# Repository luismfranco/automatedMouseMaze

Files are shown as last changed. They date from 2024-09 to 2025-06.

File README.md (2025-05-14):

# Automated Mouse Maze

GUI for behavioral and neurophysiological experiments in an automated maze for mice.  
Currently under development in the [Niell Lab](https://nielllab.uoregon.edu/).

***Disclamimer: the initial designs for this automated maze are based on previous work done at the [Sylwestrak Lab](https://www.sylwestraklab.com/)***

# Installation

## Requirements

1. Operating System: Windows.
2. [Anaconda](https://www.anaconda.com/). Set up its path to [environment variable](https://www.youtube.com/watch?v=Xa6m1hJHba0&ab_channel=DavidRajMicheal).
3. [Git](https://git-scm.com/downloads).
4. [Microsoft Visual C++ 14.0](https://visualstudio.microsoft.com/visual-cpp-build-tools/) or greater.
5. [Arduino IDE](https://www.arduino.cc/en/software/).
6. [StreamCatcherPro](https://www.startech.com/en-us/audio-video-products/usb3hdcap).
7. [Open Ephys GUI](https://open-ephys.org/gui)

## Step by step

In the Command Prompt:
1. Create your environment. Example:  
``conda create -n automatedMouseMaze python=3.10.14 pip``
2. Activate your environment:  
``conda activate automatedMouseMaze``
3. Choose a location where you would like to copy this repo. Example:  
``mkdir Documents\automatedMouseMaze\Application``  
``cd Documents\automatedMouseMaze\Application\``
4. Clone this repository:  
``git clone https://github.com/luismfranco/automatedMouseMaze.git .``
5. Before installing dependencies, you might need to upgrade pip:  
``python -m pip install --upgrade pip``
6. Install dependencies in your environment (this might take a few minutes):  
``pip install .``
7. This code was developed for Python - Teensy 4.0 communication. pyfirmata was developed for Arduino. There is bug in pyfirmata when trying to input the Teensy 4.0 layout. To fix it, run:  
``python src\debugPyFirmata.py``

If everything went well, you should be able to run the GUI:  
``python automatedMouseMaze.py``
<p align="center">
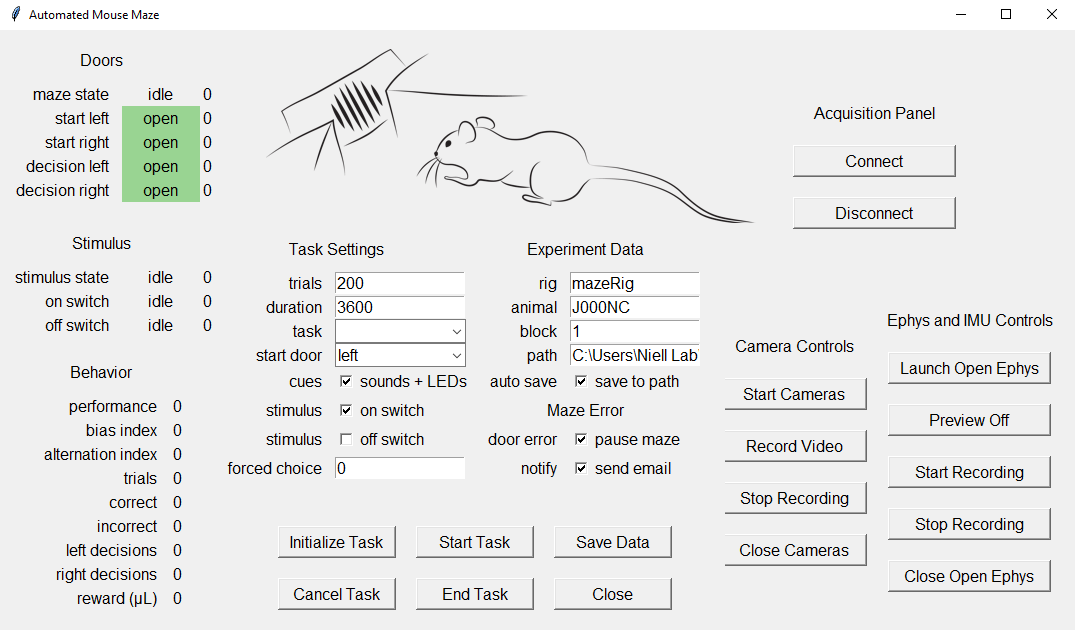
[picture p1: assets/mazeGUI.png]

</p>

However, this app requires a connection with a Teensy board in order to work. Also, the automated maze has several other components, such as IR sensors, solenoid valves, a speaker, and LEDs. To build your own maze, follow this tutorial: 
[maze construction](docs/howToBuildYourOwnMaze.md).

This apps also controls and triggers the recording of video, IMU sensors, and electrophysiology probes. Please refer to [Parker et al., 2022](https://doi.org/10.1016/j.neuron.2022.08.029) for more details on this.

# Configuration Settings

Before running your first experiment, make sure you have uploaded the [Standard Firmata](https://github.com/firmata/arduino/blob/main/examples/StandardFirmata/StandardFirmata.ino) sketch into your Teensy board, which you can find in Arduino IDE at:  
``File --> Examples --> Firmata --> Standard Firmata``

Also, ensure Teensy is properly [configured](config/package.json):
1. Under ``teensyConfiguration``, select the correct serial ``port`` for communication between the computer and Teensy (e.g. ***COM3***).
2. Under ``stimulusScreen``, select the correct ``screenNumber``. In Windows, you can verify the screen number in: ``Display settings > Display > Identify``.
3. There are also a number of input and output digintal pins under ``teensyConfiguration``. Make sure they are properly assigned according to your electronic circuit (see example below).

## Example board with connections for Teensy pins

1. Solenoid valves, including transistors and diodes. The solenoids for the maze doors (green wires) require a 24 V power supply. The solenoids for the water rewards (blue wires) require a 12 V power supply. **Important: use diodes to make sure current doesn't flow back from solenoids to Teensy**. In this example, the configuration is:  
   ``"leftStartDoor": "5"``  
   ``"rightStartDoor": "7"``  
   ``"leftDecisionDoor": "9"``  
   ``"rightDecisionDoor": "11"``  
   ``"leftWaterPort": "1"``  
   ``"rightWaterPort": "3"``  
2. IR sensors, including a connection between their white signal wire and the 5V power supply (see the bottom view of the circuit below). In this example, the configuration is:  
   ``"leftStartIRsensor": "22"``  
   ``"rightStartIRsensor": "20"``  
   ``"leftDecisionIRsensor": "18"``  
   ``"rightDecisionIRsensor": "16"``  
   ``"startStimulusIRsensor": "15"``  
   ``"stopStimulusIRsensor": "14"``  
3. LEDs, including transitors diodes and resistors. LEDs require a 5 V power supply. In this example, the configuration is:  
   ``"leftLED": "0"``  
   ``"rightLED": "2"``  

<p align="center">
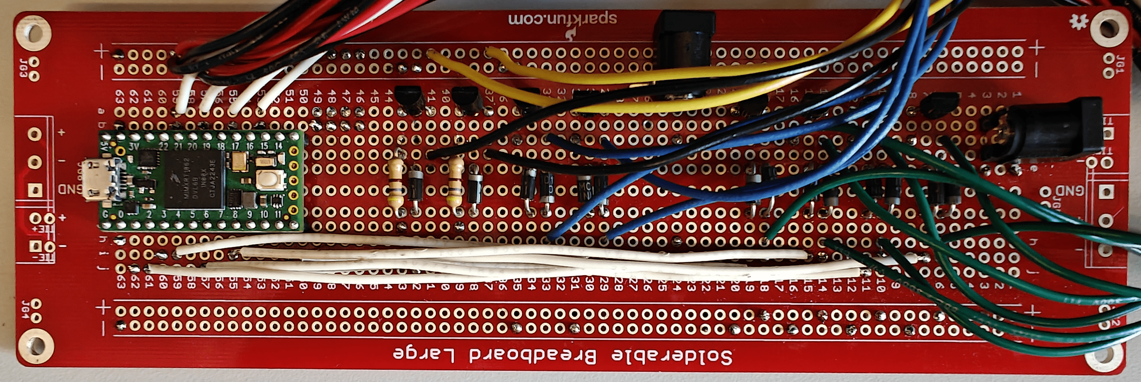
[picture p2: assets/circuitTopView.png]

</p>
<p align="center">
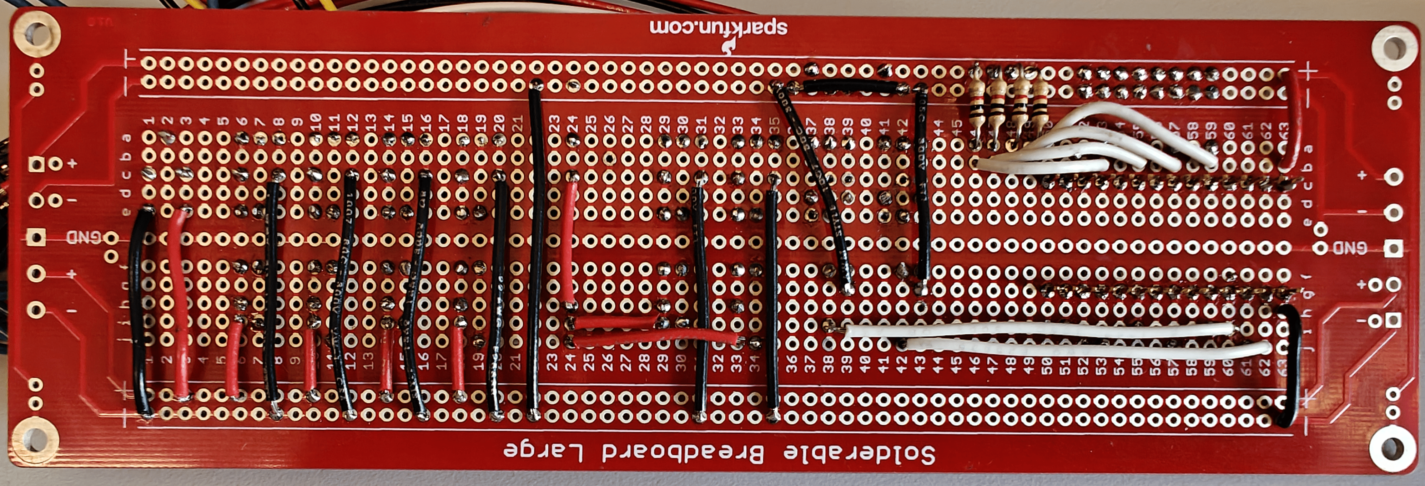
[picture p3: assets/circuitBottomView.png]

</p>

# How to Run this App

In the Command Prompt, activate your environment. Example:  
``conda activate automatedMouseMaze``  
Then, cd to the location where this app was installed, and then type:  
``python automatedMouseMaze.py``

You could also create a batch file. Example:  
``call activate automatedMouseMaze``  
``cd C:\Users\Niell Lab\Documents\automatedMouseMaze\Application\``  
``python automatedMouseMaze.py``  

# Before Running an Experiment

Under ``task``, please select ``valveCalibration`` and click on ``Initialize Task``. This will open a small window with three parameters:

<p align="center">
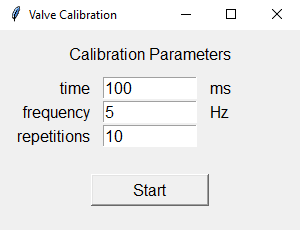
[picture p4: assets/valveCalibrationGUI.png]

</p>

1. ``time`` for the opening water valves (in ms).
2. ``frequency`` for valve openning repetitions (in Hz). Make sure ``frequency`` is slow enough to allow the full openning ``time`` in each repetition.
3. Number of ``repetitions``. The shorter the ``time`` the more ``repetitions`` are needed to minimize measurement errors.

Example parameters for a calibration curve are displayed in the terminal every time ``valveCalibration`` is initialized:  
``Time:           5,  10,  15,  20,  25,  30,  40,  50,  60,  80, 100``  
``Frequency:     25,  25,  20,  15,  15,  15,  10,  10,   5,   5,   5``  
``Repetitions: 1500, 750, 500, 400, 300, 250, 200, 150, 125, 100,  50``  

Once you have calculated the correct valve opening time for 5, 6, 7, 8, 9 and 10 μL, you can update the ``src/mazeGUI.py`` script in the "Reward" subsection of the ``__init__`` method in the  ``class mazeGUI``:  
``self.estimatedReward = 0``  
``self.leftRewardStreak = [32, 36, 41, 45, 49, 54] # in ms``  
``self.rightRewardStreak = [32, 37, 41, 46, 50, 55] # in ms``  
``self.rewardAmounts = [ 5,  6,  7,  8,  9, 10] # in μL``  

# How to Run an Experiment

There are a few options you can select before running an experiment.

## Task Settings

1. Maximum number of ``trials``.
2. Maximum ``duration`` of the experiment (in seconds).
3. The particular visual stimulus, under ``task`` (more details below).
4. The location of the animal at the start of the session, under ``start door``. This is the door that will open for the first trial.
5. Sounds and light ``cues`` for helping during learning of the task.
6. Triggering the display of the visual ``stimulus`` on the screen.
7. Turning off the display of the visual ``stimulus``.
8. Fraction of trials with ``forced choice``, where only the door for the correct decision is opened. Helpful during early stages of training.

## Experiment Data

1. Name of your ``rig``.
2. Name of your ``animal``.
3. ``block`` number.
4. ``path`` for saving the experiment data.
5. ``autoSave`` option.

Once your have selected your desired options, you can click on ``Initialize Task``. This will establish a connection between the computer and Teensy. It will also initialize the visual stimulus in the background, but it will not show it yet. Clicking on ``Initialize Task`` disables all fields in the "Task Settings" and "Experiment Data" boxes. If you would like to change something, click on ``Cancel Task``. This will allow you to access all fields again, but you will need to ``Initialize Task`` again afterwards.

Next, clikc on ``Start Task`` to start running your experiment. If you would like to record video and do electrophysiology as well (see below), make sure you have initialized those options before clickin on ``Start Task``. After a task has started, only the door selected in ``start door`` (see above) will open, and the visual stimulus will be displayed on the screen throughout the trial, unless the on and/or off switchs are enabled (see above).

If you would like to stop the task prematurely (i.e., before reaching the maximum trial number or the maximum duration), click on ``End Task``.

At the end of each experiment, if ``auto save`` is enabled, data are automatically saved. Also, if ``auto save`` is not enabled, or in case of an unexepcted crash (and if the GUI is still available), you can click on ``Save Data`` to manually save your experiment data.

To close the app GUI, click on ``Close`` or on the upper right "X".

# Camera Controls

Before using the cameras for the first time, make sure you have set their IDs properly under ``crownCameras`` in the [configuration](config/package.json) file. You can find their IDs by running this script in the Command Prompt:  
``python src\findCameras.py``  

1. ``Start Cameras`` opens a preview window for the eye and the world cameras, which record the movement of one eye of the mouse and the world in front of its head, respectively. This preview also creates temporary files in the ``path`` for saving data. Data will only be permanently saved if the ``Record Video`` button is pressed.
2. ``Record Video`` starts the recording of video from both the eye and the world cameras.
3. ``Stop recording`` stops the recording of video in both cameras.
4. ``Close Cameras`` closes the preview window.

***Important: make sure you start your video recordings before starting your task to avoid losing data***

# Ephys and IMU Controls

Before you can use these controls, make sure you have installed the [Open Ephys GUI](https://open-ephys.org/gui). Please refer to the Open Ephys [documentation](https://open-ephys.github.io/gui-docs/) to learn more about this GUI. For instance, you can begin by dragging and adding: 1) an acquisition board, 2) a record node, and 3) an LFP viewer to the signal chain at the bottom of the GUI from the list of processors on the left pannel.

<p align="center">
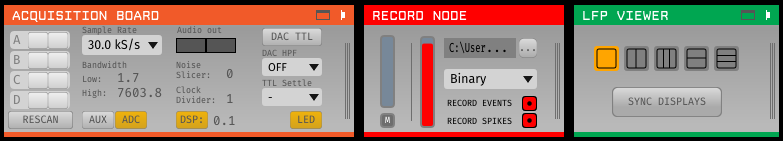
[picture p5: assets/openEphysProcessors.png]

</p>

Once you have done that, you can control the Open Ephys GUI with the buttons in the Automated Mouse Maze GUI. 

1. ``Launch Open Ephys`` launches the GUI. The GUI automatically detects the inputs to the Open Ephys acquisition board. For instance, it will automatically detect the HDMI input from the I/O board (carrying data from the IMU), and the Intan cable (carrying data from the neural probe).
2. ``Preview Off`` switches to ``Preview On`` upon clicking on it. This function allows you to see ongoing neural activity and IMU signals without the need to record them.
3. ``Start Recording`` starts a new recording.
4. ``Stop Recording`` stops recording in progress. Data are automatically saved once the recording is stopped.
5. ``Close Open Ephys`` closes the Open Ephys GUI.

***Important: make sure you start your ephys recordings before starting your task to avoid losing data***

# Task

As mentioned above, the option ``task`` allows you to select between 4 different built-in tasks:

1. Drifting gratings (based on Psychopy [https://github.com/psychopy/psychopy]).
2. Motion selectivity (based on Psychopy [https://github.com/psychopy/psychopy]).
3. White noise (based on OpenCV https://github.com/opencv/opencv).
4. Object discrimination (based on Pygame [https://github.com/pygame/pygame], and on ModernGL [https://github.com/moderngl/moderngl]).
5. There is also another option for calibrating your solenoid valves (see section above).

It is easy to change the settings for the [drifting gratings](src/driftingGratings.py), [motion selectivity](src/motionSelectivity.py) and [white noise](src/whiteNoise.py) tasks under their respective ``initializeStimulus`` and ``startStimulus`` methods. Please refer to Psychopy documentation to learn more about the available options for [GratingStim](https://www.psychopy.org/api/visual/gratingstim.html) and [DotStim](https://www.psychopy.org/api/visual/dotstim.html).

# While Task is Running

The app GUI displays general maze information and behavior stats on the left-hand side that continuously update through the experiemntal session.

## Doors

1. ``maze state``. (0) *ready*, before session starts running, (1) *start*, once a trial has started, (2) *end*, once the mouse has made a decision, (3) *ITI-left*, mouse is on the left side of the maze, waiting for the *left start door* to open, (4) *ITI-right*, mouse is on the right side of the maze, waiting for the *right start door* to open.
2. ``start left``. displays *open* or *closed* for the *left start door*. It also displays the state of its corresponding beam break, a (0) indicates the mouse is passing through its beam break, otherwise it shows (1).
3. ``start right``. same, but for the *right start door*.
4. ``decision left``. same, but for the *left decision door*.
5. ``decision right``. same, but for the *right decision door*.

## Stimulus

1. ``stimulus states``. (0) *ready*, before session starts running, (1) a trial has started, it can display *on* or *off* depending on the configuration for the stimulus *on switch*, (2) *on*, either the stimulus has been on since trial start, or the stimulus just turned on when the mouse passed the *on switch* beam break, (3) the mouse just passed the *off switch* beam break, it can display *on* or *off* depending on the configuration for the stimulus *off switch*, (4) waiting for a decision to be made, (5) "ready", ITI, waiting for a new trial to begin.
2. ``on switch``. if its box is checked, it will display when the stimulus is turned "on" and "off" by the corresponding beam breaks.
3. ``off switch``. if its box is checked, it will display "on" when the stimulus is intentionally turned off by the second beam break in the central corridor of the maze. It will display "off" once a decision has been made by the mouse.

**Note: positioning the beam breaks for the *on* and *off* switches along the central corridor of the maze allows for different experimental configurations, where attention to the visual stimuli can be triggered at different locations, or, to test working memory, the visual stimulus can also be removed at different locations.**

## Behavior

1. ``performance``. Mouse performance, calculated as *P = C / (C + I)*, where *C* and *I* are the total number of correct and incorrect decisions, respectively.
2.  ``bias index``. Decision bias, calculated as *BI = (L - R) / (L + R)*, where *L* and *R* are the total number of left and right decisions, respectively.
3.  ``alternation index``. Rate of switching between decisions (e.g. L, R, L, R, L, R, ...), calculated as *AI = sum(abs(diff(D)))/length(D)*, where *D* is a sequence of zeros and ones corresponding to L and R decisions.
4.  ``trials``. Trial number.
5.  ``correct``. Number of correct decisions.
6.  ``incorrect``. Number of incorrect decisions.
7.  ``left decisions``. Number of decisions to the left.
8.  ``right decisions``. Number of decisions to the right. 
9.  ``reward (μL)``. Estimated reward, based on the parameters obtained by the calibration curve.

# Behavior Data File

Data are automatically saved at the end of a session in the desired path as a pickle file. This file contains a Pandas DataFrame with the following fields:

1. ``trial`` number.
2. ``startDoor`` for each trial. (0) for left, (1) for right.
3. ``leftTargetProbability`` for each trial. Probability for displaying the target object associated with the left decision.
4. ``target`` object for each trial. (0) for left, (1) for right.
5. animal's ``decision`` for each trial. (0) for left, (1) for right.
6. ``forcedChoice`` for each trial. (0) for no forced choice, (1) for forced correct choice.
7. ``correct`` trial identifier. (0) for incorrect trial, (1) for correct trial.
8. ``trial type``: identifier for correct left (1), incorrect right (2), incorrect left (3), or correct right trials (4).
9. ``startTime``. Time stamp for the start of each trial: opening of start door.
10. ``endTime``. Time stamp for the end of each trial: closing of decision door.
11. ``stimulusStartTime``. Time stamp for the display of the visual stimulus on the screen (if option is enabled).
12. ``stimulusEndTIme``. Time stamp for turning off the display of the visual stimulus (if option is enabled).
13. ``taskRawStartTime``. Time stamp for the start of the task. Important for synchronization with video and electrophysiology recordings.

In addition, **task settings** and **visual stimulus parameters** are saved in the same DataFrame. These include the input values for the fields in ``task settings`` and ``experiment data``, the values for water rewards obtained from the ``calibration curves``, as well as specific parameters for the **visual stimulus** defined by the corresponding ``task``.

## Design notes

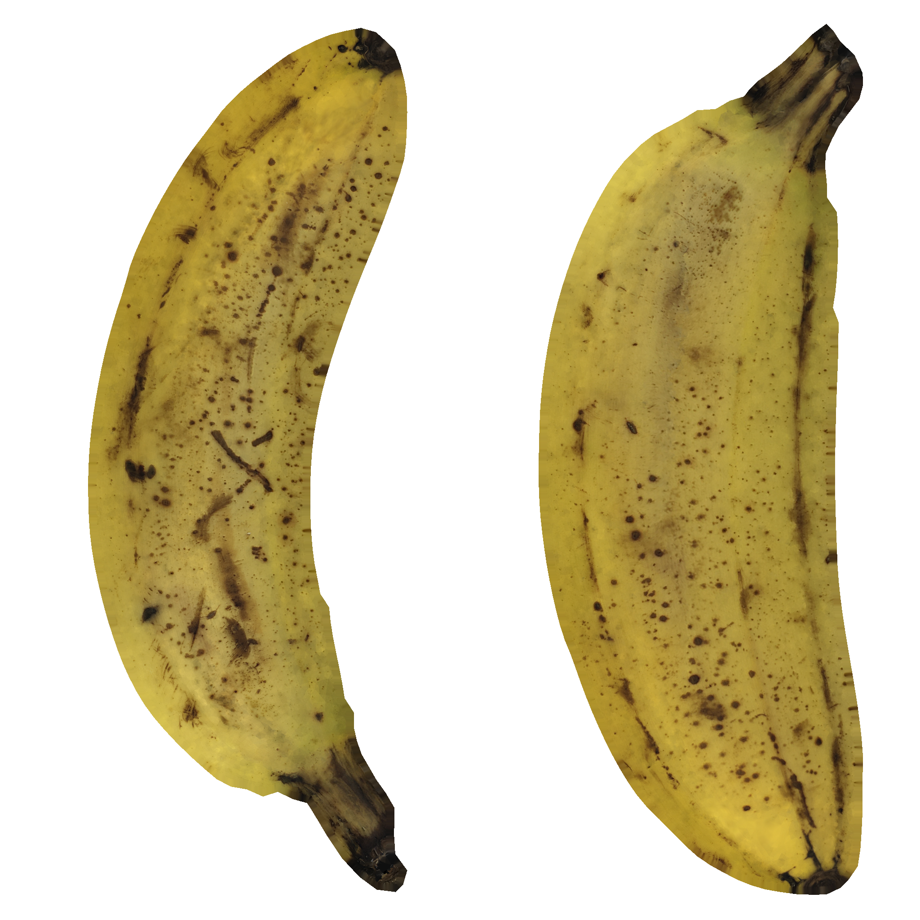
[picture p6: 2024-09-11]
assets/banana/banana.png

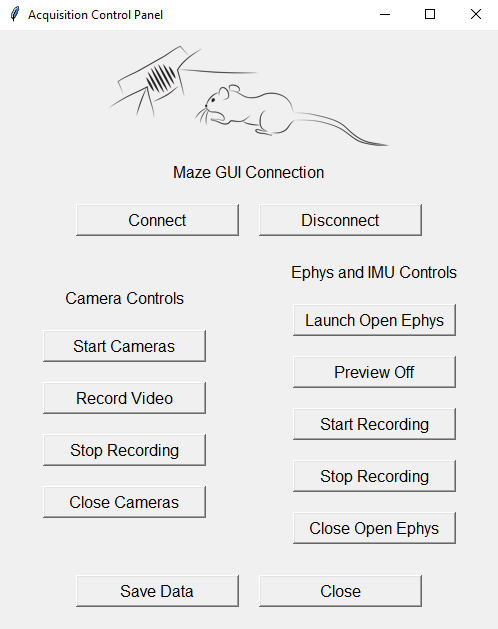
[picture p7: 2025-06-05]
assets/acquisitionControlPanelGUI.png

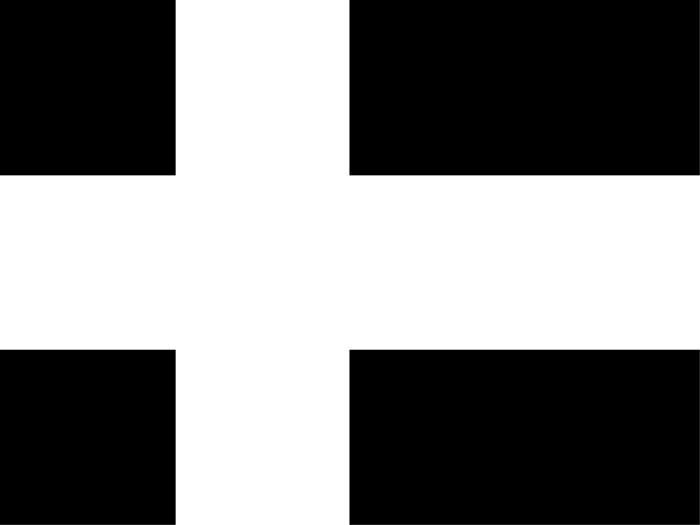
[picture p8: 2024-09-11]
assets/whitebox/whiteBox.png

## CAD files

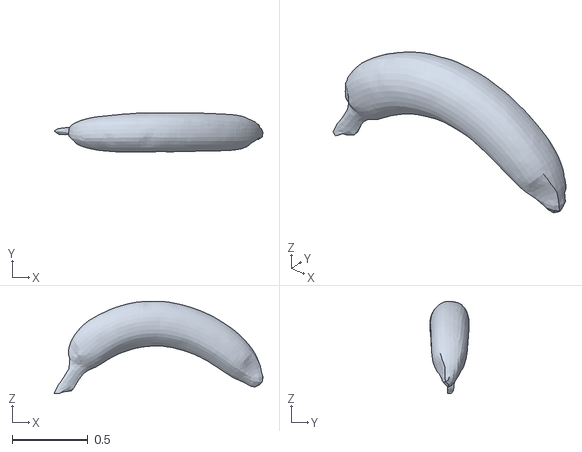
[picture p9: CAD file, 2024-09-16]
assets/banana/banana.obj
1.38 x 0.26 x 0.61

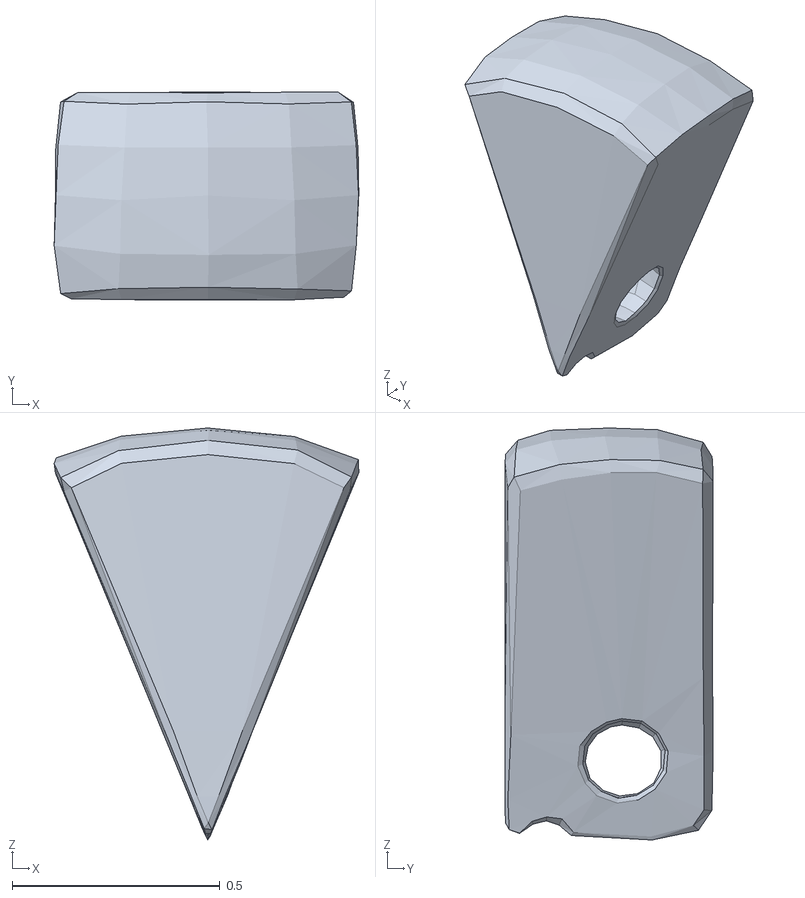
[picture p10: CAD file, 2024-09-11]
assets/cheese/cheese.obj
0.733 x 0.502 x 0.991

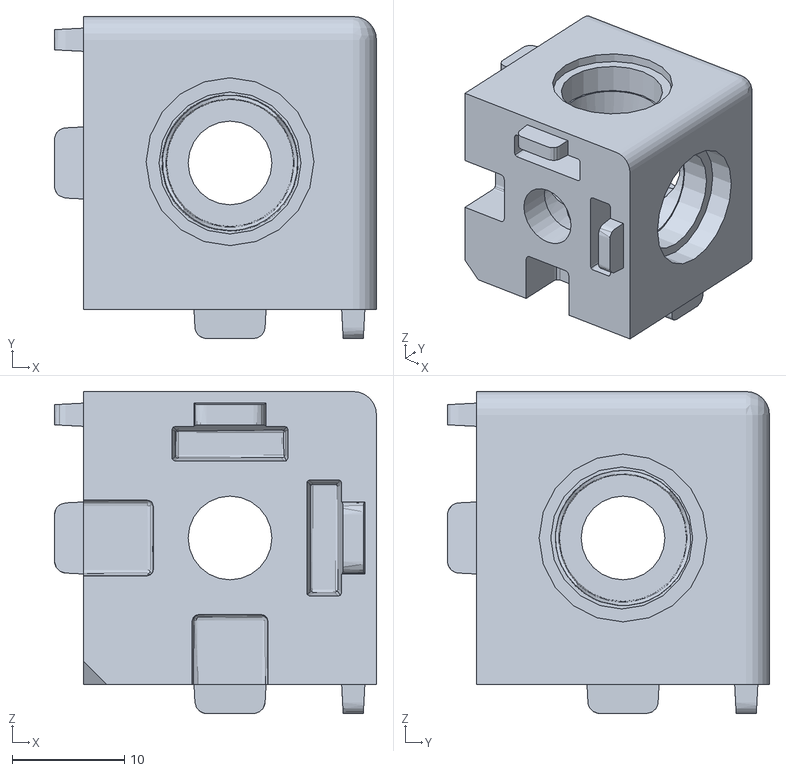
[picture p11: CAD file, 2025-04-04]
assets/hardware/cornerEndBraket.stl
28.8 x 28.8 x 28.8

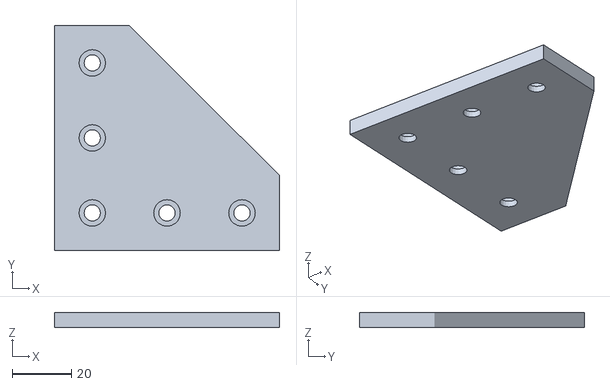
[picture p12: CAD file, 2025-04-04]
assets/hardware/cornerSurfaceBracket.stl
76.2 x 76.2 x 5.00

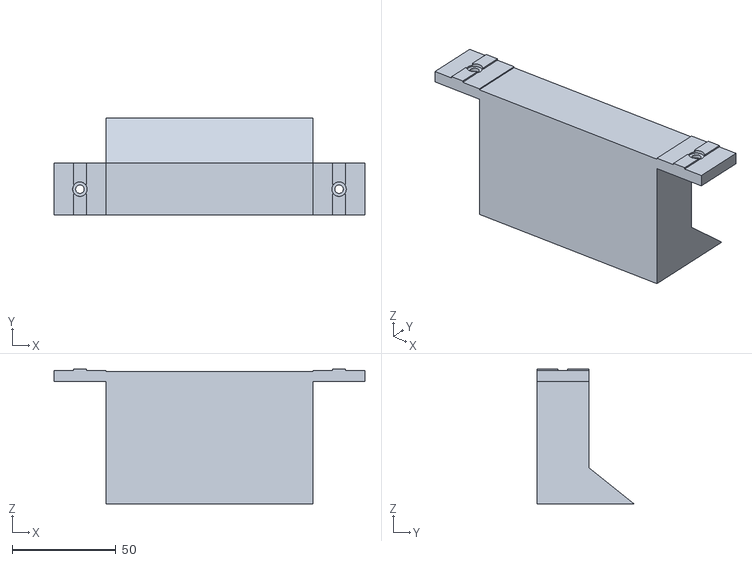
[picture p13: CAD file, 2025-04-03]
assets/hardware/doorFloorStop R.stl
150.0 x 46.8 x 65.0

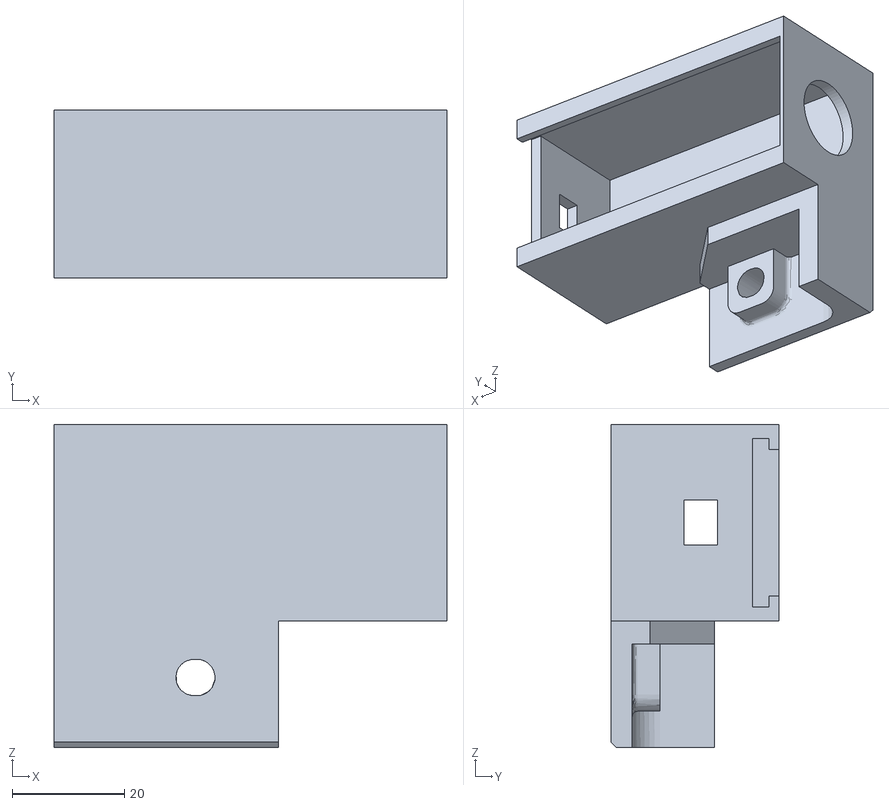
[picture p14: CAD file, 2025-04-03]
assets/hardware/waterButtonBox L.stl
70.0 x 30.0 x 57.6

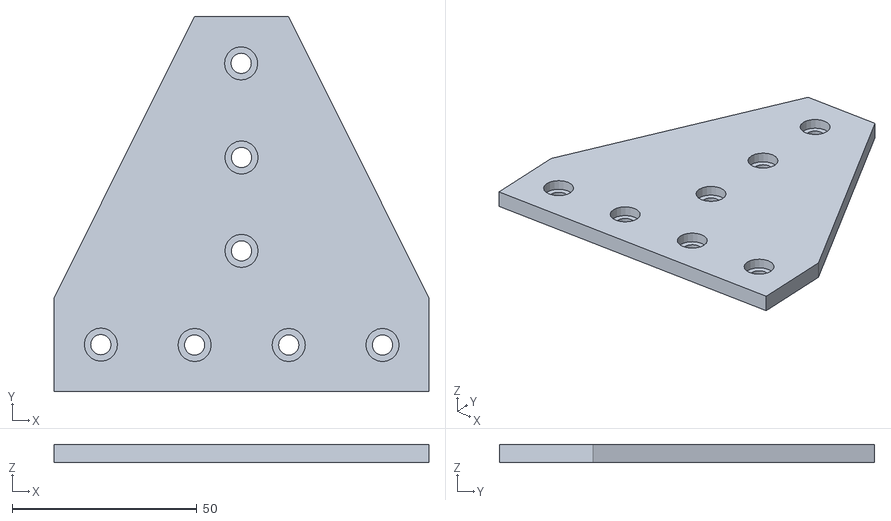
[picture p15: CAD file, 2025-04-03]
assets/hardware/surfaceBracket.stl
101.6 x 101.7 x 5.00

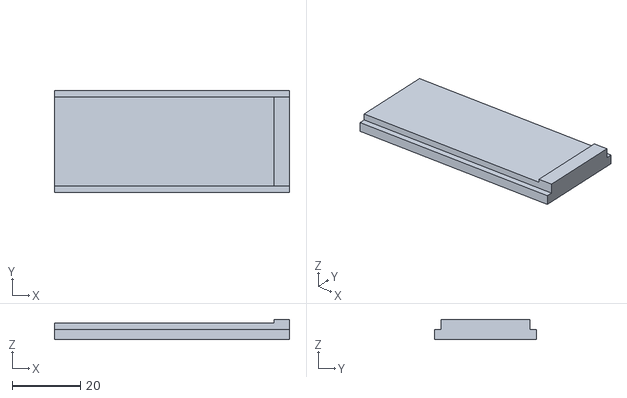
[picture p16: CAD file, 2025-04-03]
assets/hardware/waterButtonBoxLid.stl
69.0 x 30.0 x 5.90

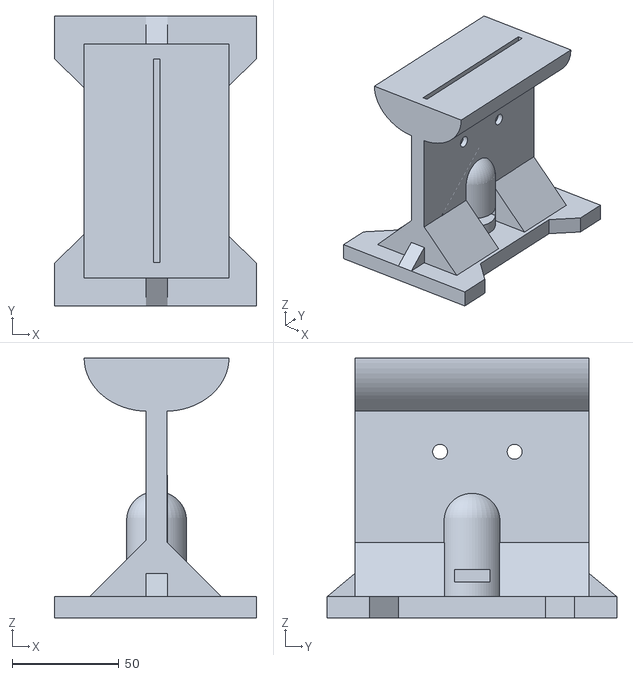
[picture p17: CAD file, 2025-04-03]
assets/hardware/doorHolder.stl
95.0 x 136.0 x 122.0

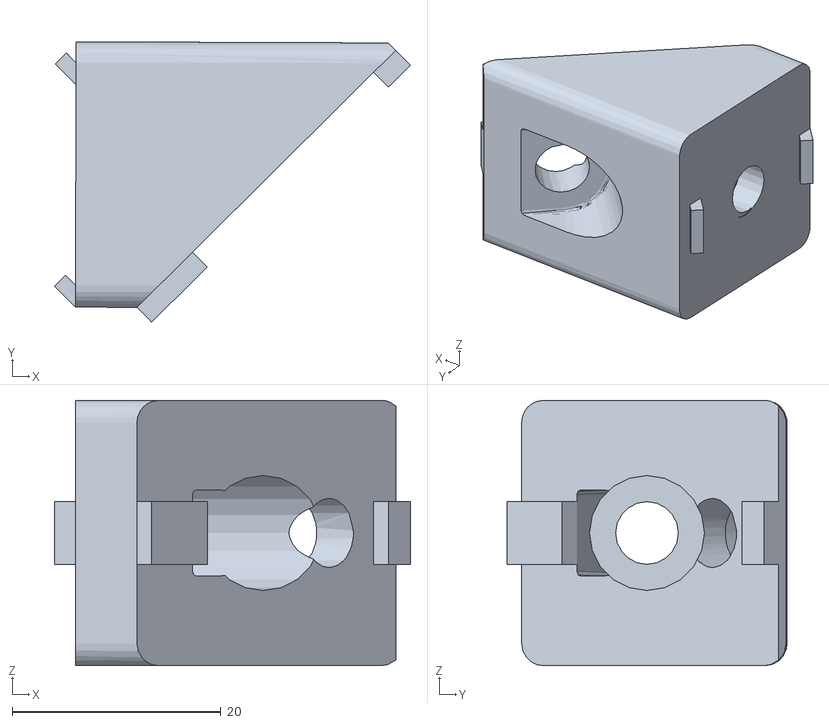
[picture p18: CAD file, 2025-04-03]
assets/hardware/45degreeBracket.stl
34.1 x 26.8 x 25.4

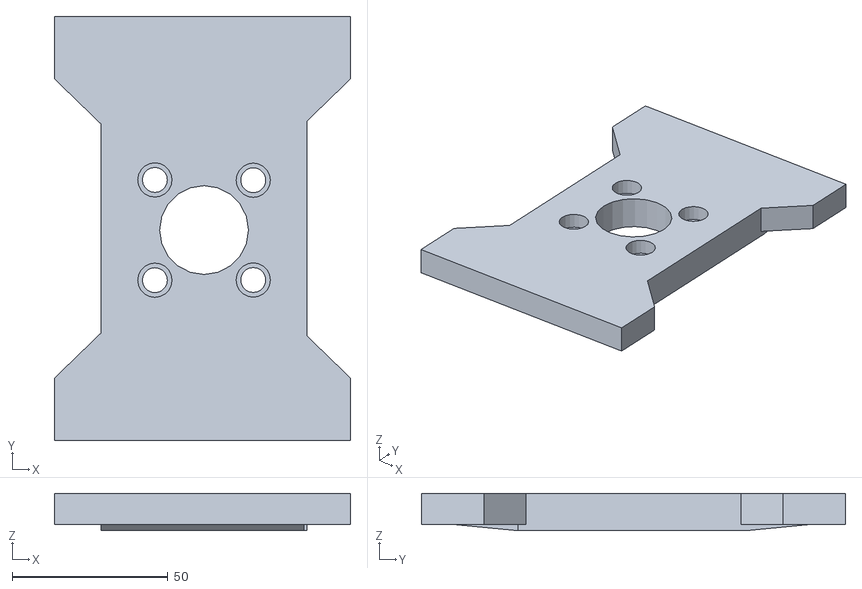
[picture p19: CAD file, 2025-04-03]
assets/hardware/doorCylinderStop.stl
95.0 x 136.0 x 12.0

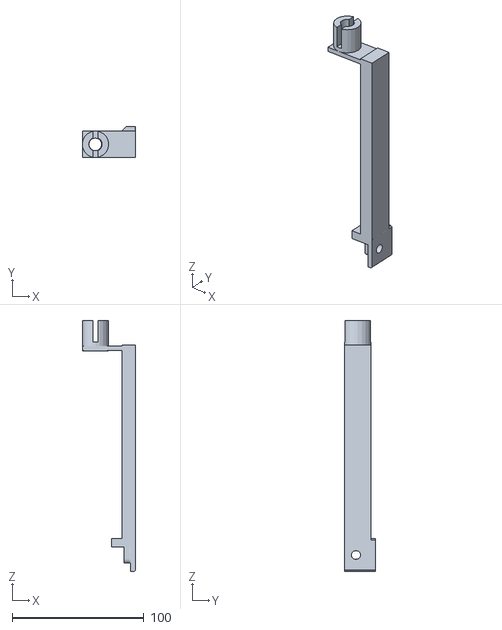
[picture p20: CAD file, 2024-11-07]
assets/hardware/syringeHolder.stl
40.5 x 23.5 x 190.2

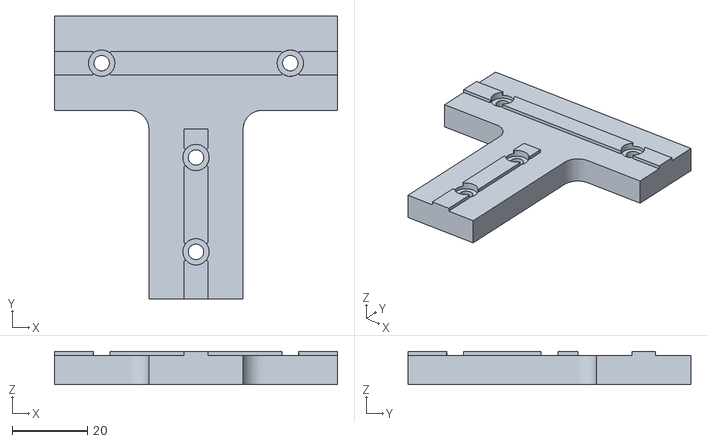
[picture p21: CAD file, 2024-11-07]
assets/hardware/Tbracket.stl
75.0 x 75.0 x 8.75

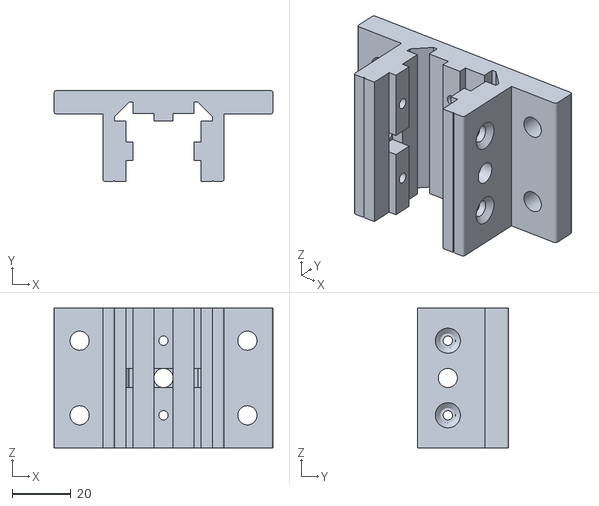
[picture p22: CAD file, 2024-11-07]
assets/hardware/TslottedSleeve.stl
74.6 x 30.9 x 47.6

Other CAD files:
assets/hardware/doorFloorStop L.stl
assets/hardware/waterButtonBox R.stl
assets/hardware/cylinderMountingBase.stl
assets/hardware/waterPort.stl
assets/hardware/IRsensorHolder L.stl
assets/hardware/IRsensorHolder R.stl
assets/hardware/circuitBox.stl
assets/hardware/circuitBoxLid.stl
assets/hardware/screenHolders.stl
assets/hardware/valveHolder.stl

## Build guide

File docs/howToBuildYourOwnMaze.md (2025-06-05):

# Maze Construction

This tutorial describes how we built our autoamted maze in the [Niell Lab](https://nielllab.uoregon.edu/).

***Important: this tutorial is currently under development***

<p align="center">


</p>

# Components

## Maze

1. 1" T-slotted [squared](https://www.mcmaster.com/47065T101/) and [rounded](https://www.mcmaster.com/3136N27/) framing rails, cut to a custom size with 1/4"-20 threads on both ends.
2. Sign white 9 % light transmission [acrylic](https://www.tapplastics.com/product/plastics/cut_to_size_plastic/acrylic_sheets_color/341) for the floor, walls and doors of the maze.
3. 1" [brakets](https://www.mcmaster.com/47065T236/) and [cubes](https://www.mcmaster.com/47065T244/) to assemble the structural frame of the maze.
4. A white melamine [wood shelf](https://www.homedepot.com/p/White-Melamine-Wood-Shelf-23-75-in-D-x-48-in-L-252297/202089063) with 2" [caster wheels](https://www.amazon.com/Casters-Locking-Castors-Furniture-Kitchen/dp/B09QZMTSCQ/ref=pd_bxgy_img_d_sccl_2/142-9516444-0421340?pd_rd_w=h5m3x&content-id=amzn1.sym.839d7715-b862-4989-8f65-c6f9502d15f9&pf_rd_p=839d7715-b862-4989-8f65-c6f9502d15f9&pf_rd_r=FRMHFY3ZBWA5QW7X6ASM&pd_rd_wg=8v5Oh&pd_rd_r=5618abc9-7d00-4d7a-a696-668fa49b88b9&pd_rd_i=B0BFXLTQNH&th=1) for the base of the maze.
5. A 10" [screen](https://www.amazon.com/dp/B0987468N2/ref=sspa_dk_detail_4?pd_rd_i=B0987468N2&pd_rd_w=QqC5K&content-id=amzn1.sym.386c274b-4bfe-4421-9052-a1a56db557ab&pf_rd_p=386c274b-4bfe-4421-9052-a1a56db557ab&pf_rd_r=1QH3Q0EH5X5P3PGTJ3EK&pd_rd_wg=wrki0&pd_rd_r=280cd8b9-b4b4-4a81-84ca-9a71bb273634&s=pc&sp_csd=d2lkZ2V0TmFtZT1zcF9kZXRhaWxfdGhlbWF0aWM&th=1) for displaying visual stimuli.
6. Mini USB [speaker](https://www.adafruit.com/product/3369?gclid=Cj0KCQjw9fqnBhDSARIsAHlcQYQN7-PUcKRt7g5K4LZLOxeUrOmGBO-mkdPEippvQnJ8RdAV6c8ZS8oaAvPWEALw_wcB) for signaling correct and incorrect trials.
7. Diffused 5 mm [LEDs](https://www.adafruit.com/product/4203?gclid=Cj0KCQjw9fqnBhDSARIsAHlcQYQOVymyhPb8JML-s9yA5havhJG0yBzvc3udh55acPwMJ-_8xEU4wKcaAnpeEALw_wcB) for signaling correct trials.
8. [Solenoid valves](https://www.theleeco.com/industries/scientific-instruments/products/solenoid-valves/browse/?filters[subtype][]=Control+Solenoid+Valves) for control of water delivery.
9. 1/16" ID x 1/8" OD Tygon [tubing](https://www.usplastic.com/catalog/item.aspx?itemid=91104&catid=864) for the water delivery system.
10. 14 gauge luer-lock blunt tip [needles](https://www.amazon.com/Syringe-Dispensing-Needles-Length-Interface/dp/B07DZC225B/ref=pd_ci_mcx_di_int_sccai_cn_d_sccl_2_1/133-0408013-9182656?pd_rd_w=JuARf&content-id=amzn1.sym.751acc83-5c05-42d0-a15e-303622651e1e&pf_rd_p=751acc83-5c05-42d0-a15e-303622651e1e&pf_rd_r=SDJGVFYGQZ0KS2EZG109&pd_rd_wg=XP1nb&pd_rd_r=9ea53b80-e963-4a30-bfc5-857ae6b058f9&pd_rd_i=B07DZC225B&psc=1) as spouts for water delivery.
11. Custom [3D-printed objects](https://github.com/luismfranco/automatedMouseMaze/tree/99c225861e82ac3776c7e1dc496d73c4fc0f3bcc/assets/hardware) as rail brakets, sections of walls (i.e., water ports, stimulus screen holders), and to mount other components (i.e., IR sensors, speaker, cables, water system).
12. A blackout [curtain](https://evertrack.co/blackout-room-divider-curtain-eclipse-satin/?utm_term=&utm_campaign=PMAX+-+Room+Divider+Curtains&utm_source=adwords&utm_medium=ppc&hsa_acc=5806130293&hsa_cam=22123857351&hsa_grp=&hsa_ad=&hsa_src=x&hsa_tgt=&hsa_kw=&hsa_mt=&hsa_net=adwords&hsa_ver=3&gad_source=1&gclid=Cj0KCQjw4v6-BhDuARIsALprm32yAWsM92bhXs5Hm0Y3QMyoQlhOliOSD0VcVHp_9gU-yHXiStgtKXEaAvcoEALw_wcB) and [rail](https://www.amazon.com/dp/B0C69LGQW1/ref=sspa_dk_detail_2?pd_rd_i=B0C69LGQW1&pd_rd_w=YEFyC&content-id=amzn1.sym.386c274b-4bfe-4421-9052-a1a56db557ab&pf_rd_p=386c274b-4bfe-4421-9052-a1a56db557ab&pf_rd_r=B9N6694BX21GFFRSVHP6&pd_rd_wg=QsIWq&pd_rd_r=c0aed70f-5ff7-4f5d-a2dd-321a2899c61f&s=kitchen&sp_csd=d2lkZ2V0TmFtZT1zcF9kZXRhaWxfdGhlbWF0aWM&th=1) to isolate the maze and mice from external distractions.

## Automated Doors

1. [Pneumatic actuators](https://www.amazon.com/Baomain-Pneumatic-Cylinder-SC-Screwed/dp/B01F9XZQ1K/ref=pd_ci_mcx_di_int_sccai_cn_d_sccl_2_2/136-8001444-7379768?pd_rd_w=CoJWI&content-id=amzn1.sym.751acc83-5c05-42d0-a15e-303622651e1e&pf_rd_p=751acc83-5c05-42d0-a15e-303622651e1e&pf_rd_r=AXNT0SNVR13YJT89ZTJJ&pd_rd_wg=F8NEU&pd_rd_r=9dcf470c-de43-4689-a980-ca5e8e994869&pd_rd_i=B01F9XZQ1K&th=1) for movement of the automated doors.
2. A [solenoid manifold](https://www.amazon.com/Baomain-4V210-08-Position-Pneumatic-Solenoid/dp/B01D9IGCTC/ref=sims_dp_d_dex_ai_speed_loc_mtl_v4_d_sccl_4_1/136-8001444-7379768?pd_rd_w=QAJm3&content-id=amzn1.sym.af515e1d-64ab-47a5-8a2e-6be4d0f4cdc5&pf_rd_p=af515e1d-64ab-47a5-8a2e-6be4d0f4cdc5&pf_rd_r=QQ6ZJF00XSNFZP6H8B3Z&pd_rd_wg=ip6Yj&pd_rd_r=6282a60c-3df6-4d58-8258-af29a286d7ae&pd_rd_i=B01D9IGCTC&psc=1) for controlling the automated doors.
3. [6 mm](https://www.amazon.com/Tailonz-Pneumatic-Black-Polyurethane-32-8ft/dp/B08GC6TR2S/ref=sr_1_6?crid=B4SJCL6S8C9C&dib=eyJ2IjoiMSJ9.DejGkL7N9ogqAzdCGOySW8Ul4oFXYI6uTvpMsLFLQavsPcgyc9dCZSS0RZEDuOVTGBNc74dp5AgyndprPP87Hf5uJyTtiH9rcP7fQU8OTkzCA8K8Lv6_3velU18rnE5GaAfLZ6q1gyariRIkULl7URyfKc2KDw0pVo_LMPqGbvt8MmwsfXPHnCfzkYaMb4eLXCrkmvK0VoPedBBdU368PWvUj1i6hELtX5D_il5MeDzO23k3WryqV_aB2wbEvVOaP6Nks4V_xsxegeLF3uYnt_uTJ9Vwoqsxe3ukTBuhLVI.ajZ5AaE_mu1l8TI9caTWLeYIIOOZVvQAvAvGWvogzXg&dib_tag=se&keywords=Air%2BLine%2BTubing%2BKit%2B6mm%2Bblack&qid=1714772204&s=industrial&sprefix=air%2Bline%2Btubing%2Bkit%2B6mm%2Bblac%2Cindustrial%2C121&sr=1-6&th=1) and [8 mm](https://www.amazon.com/CGELE-Pneumatic-Transfer-OD-39-4Ft-12Meter/dp/B09LS1S7MK/ref=sr_1_3?crid=1UCLWG8RC00F5&dib=eyJ2IjoiMSJ9.9IT0mdNrbcPPwFnwS3lttd1-X4Lt2TRh2Ekuy9jjREetTrO9R6abyOPbWKJOIBw0.COukHekBEaDTeMd4yj45MHDLXDYYBJPRxJqthZbJgoc&dib_tag=se&keywords=TAILONZ%2BPNEUMATIC%2BBlack%2B5%2F16&qid=1724450805&s=hi&sprefix=tailonz%2Bpneumatic%2Bblack%2B5%2F1%2Ctools%2C144&sr=1-3&th=1) tubing for air connections, as well as [adapters](https://www.amazon.com/Metalwork-Straight-Reducing-Pneumatic-Connector/dp/B07C7BGQ9S/ref=sr_1_5?crid=2EOM3OXEO5504&dib=eyJ2IjoiMSJ9.sZVireplGplt2H6sWKEogbyxddOqDaPAou-Hecj9GtV1WioAia-WJQIGtxOWdVFVTQup_Kqhm3tuUmI4i797ggSqxKtK6BQcITqGEm_J8Jd80-lc9OO1TKfBGQq-wL9LLAby1xOZYYVYpjkhlgDVuNfve2of7sbq0TFmEraXme2kNnz8YlwITV7zWLn_CfpviRaNwQc0ZqtmgVXMZVcHYADlHSF5U06SYpBPrxmvLaM.iJ10JiNAwGi4COcf2CwCBSLYdg1aO_1qU6pIi8fo8Nk&dib_tag=se&keywords=10%2Bmm%2Bto%2B6%2Bmm%2Bair%2Btubing%2Badapter&qid=1724450958&sprefix=10%2Bmm%2Bto%2B6%2Bmm%2Bair%2Btubing%2Badapter%2Caps%2C214&sr=8-5&th=1).
4. Air flow [control valves](https://www.amazon.com/dp/B0BMFV48YB/ref=sspa_dk_detail_1?pd_rd_i=B0BMFSYB5Q&pd_rd_w=VSRTa&content-id=amzn1.sym.8c2f9165-8e93-42a1-8313-73d3809141a2&pf_rd_p=8c2f9165-8e93-42a1-8313-73d3809141a2&pf_rd_r=2GSZVHJ84JHSYXGXWF79&pd_rd_wg=rD2xV&pd_rd_r=86c33250-2e60-44ee-addf-e33c132e3863&s=hi&sp_csd=d2lkZ2V0TmFtZT1zcF9kZXRhaWw&th=1) for controlling the speed of the doors.
5. A [regulator](https://www.amazon.com/dp/B09MLMFF2K/ref=sspa_dk_detail_4?pd_rd_i=B09MLMFF2K&pd_rd_w=U3UuV&content-id=amzn1.sym.8c2f9165-8e93-42a1-8313-73d3809141a2&pf_rd_p=8c2f9165-8e93-42a1-8313-73d3809141a2&pf_rd_r=DGYB1C9ZMZ9F3ED5QBE2&pd_rd_wg=BIhvv&pd_rd_r=dd296391-c469-481f-a3ac-71e60c75697b&s=industrial&sp_csd=d2lkZ2V0TmFtZT1zcF9kZXRhaWw&th=1) for setting the input air pressure to the solenoid manifold.
6. IR [beam breaks](https://www.adafruit.com/product/2167) for detecting the mouse traverse through the maze.
7. 100 cm M/M [wires](https://www.amazon.com/EDGELEC-Breadboard-Optional-Assorted-Multicolored/dp/B07GD1W7XV/ref=sr_1_1_sspa?crid=1D6I1EZM32X2T&dib=eyJ2IjoiMSJ9.tjHxIQLJsk16_0YVtUGN6YeXdt0VqIwh7Zmfzd7nvfTaoSMecktPIPsgfi6eLwfPrpE-Z7TFF3Gb6OmAsEyH4OuRfeKQ2U6yeUaDnbuFGswrOXPukg3xDJGZqP0xiogOAQo_2PqBlSW5yXpFgDqxkBzMUHsNNzfc4F-zrGIxkpvzX6CnOzBpjidBHCxZRSphsHbICibgDRfXkQytRIVXbw9Gbyz2Bt6wmlDkohLT7gUYbs8jQcpc5IITMBIXfrioVjBJ50nB4BJkOvXv_kzaIx5H3ulgZPomOofbuDLn7Cw.BAJcuUxcOIL5un-H80QwuIrBCIlUhJ-gg4DElPhICeA&dib_tag=se&keywords=jumper%2Bwires&qid=1718926518&s=industrial&sprefix=jumper%2Bwire%2Cindustrial%2C148&sr=1-1-spons&sp_csd=d2lkZ2V0TmFtZT1zcF9hdGY&th=1) and 1" F/F [wires](https://www.digikey.com/en/products/detail/pololu-corporation/3860/10451018) for connections between IR sensors, water valves and LEDs to the Teensy circuit.
8. 12" M/M [wires](https://www.digikey.com/en/products/detail/pololu-corporation/1765/10450795) and 2" M/F [wires](https://www.digikey.com/en/products/detail/pololu-corporation/3845/10451009) for connections between the solenoid manifold and the Teensy circuit.
9. Custom [3D-printed objects](https://github.com/luismfranco/automatedMouseMaze/tree/99c225861e82ac3776c7e1dc496d73c4fc0f3bcc/assets/hardware) to mount the pneumatic actuators, to cushion and limit the range of motion of actuators, and to secure the acrylic doors to the actuators.
10. Foam [cushioning](https://www.amazon.com/Adhesive-Neoprene-Insulation-Furniture-Speakers/dp/B0CRQXWQVW/ref=sr_1_31?crid=1WAQENVGHAASI&dib=eyJ2IjoiMSJ9.xDBOrBm9YUYY52LlaKfoQZn7treA9NnboDS11bCZ1cS9WmyQNHZTXRrBV4mlwpaAVph5KWOLrZbCAz2k90Mw6IzJ3utfqgWq1d8K4ecApASypii6IHid7ceR9PI5BXThcq9WOmjDtjo4oupGnWj-pRGjheNhrXRMeZC-p__gf4SVxP2Ux_uf0FCsYi_BwsTJSVMe0bS4_WVuybONPMA-5H3so1UD-ifczPZHejo4v5QF1G60yC5xKDJBZKmKJecARzT7cGBr_sFQvAXn8t14im2XqmQXeDD8HagM82Hahu7wz5YRcz7_7jkRdiW9zGMuDFSm3ZyhervMte6CfHMUtMaYyjSsXuQKA8THTfEcsoVsjId5ZDDMHxb-q56tKma9OloKk3uxEIa89kH3iP9oPkKtxbOWncpXTuoaDst85lRNTO9hJL9YGzMSj0idDu_W.fZk5Qenglkk0ea6LycULhD6u9rnjPPaIzF6gw3f70w0&dib_tag=se&keywords=black%2Bfoam%2Bcushion%2Bpads%2Bwith%2Bglue&qid=1734548418&sprefix=black%2Bfoam%2Bcushion%2Bpads%2Bwith%2Bglu%2Caps%2C205&sr=8-31&th=1) for buffering the contact between 3D-printed objects that limit the range of motion of doors.

<p align="center">


</p>

## Teensy Circuit

1. [Teensy 4.0](https://www.sparkfun.com/teensy-4-0-headers.html) for processing inputs and outputs between the computer and the different components in the maze.
2. [Bread board](https://www.digikey.com/en/products/detail/sparkfun-electronics/PRT-12699/5762439?utm_adgroup=&utm_source=google&utm_medium=cpc&utm_campaign=PMax%20Shopping_Product_High%20ROAS%20Categories&utm_term=&utm_content=&utm_id=go_cmp-20222717502_adg-_ad-__dev-c_ext-_prd-5762439_sig-CjwKCAjwr7ayBhAPEiwA6EIGxH0-nJ1QtJauifHs8d_4uKSnMKyhCQBnSeDmUdDhgQHYUU73eKNs0RoCaYkQAvD_BwE&gad_source=1&gclid=CjwKCAjwr7ayBhAPEiwA6EIGxH0-nJ1QtJauifHs8d_4uKSnMKyhCQBnSeDmUdDhgQHYUU73eKNs0RoCaYkQAvD_BwE) for building the circuit.
3. NPN [transistors](https://www.digikey.com/en/products/detail/onsemi/BC547B/976366?gclsrc=aw.ds&&utm_adgroup=&utm_source=google&utm_medium=cpc&utm_campaign=PMax%20Shopping_Product_Medium%20ROAS%20Categories&utm_term=&utm_content=&utm_id=go_cmp-20223376311_adg-_ad-__dev-c_ext-_prd-976366_sig-Cj0KCQjwna6_BhCbARIsALId2Z3kIKITUhCn-wMSlmMyu4jYOpSJW8IkK0eGusF3LZLZWlHe61VJmvIaArZBEALw_wcB&gad_source=1&gbraid=0AAAAADrbLlj3So7FqTBK4QOOqqITi_jpy&gclid=Cj0KCQjwna6_BhCbARIsALId2Z3kIKITUhCn-wMSlmMyu4jYOpSJW8IkK0eGusF3LZLZWlHe61VJmvIaArZBEALw_wcB&gclsrc=aw.ds) for control of door and water solenoids with digital outputs from Teensy.
4. [Diodes](https://www.sparkfun.com/diode-rectifier-1a-50v-1n4001.html) to prevent current from flowing back from solenoids to Teensy.
5. 1k Ohm [resistors](https://www.digikey.com/en/products/detail/stackpole-electronics-inc/CFM12JT1K00/1741880) for connections related to IR sensors.
6. 470 Ohm [resistors](https://www.digikey.com/en/products/detail/stackpole-electronics-inc/CF12JT470R/1741161) for connections realted to LEDs.
7. DC barrel jack [adapters](https://www.sparkfun.com/dc-barrel-jack-adapter-breadboard-compatible.html) for power supplies.
8. Assortment of colored [wire](https://www.sparkfun.com/hook-up-wire-assortment-stranded-22-awg.html) for connections.
9. Male and female [header connector kit](https://www.amazon.com/CHENBO-Connector-Housing-Assortment-Terminal/dp/B077X8XV2J/ref=sr_1_3?crid=Q1JQUBJIDW2O&dib=eyJ2IjoiMSJ9.ZV2pcL1tMHr0QntbhCHwV0ABU5A0mO3nzz47YRlN1eukhLKB1KxTg8RLTuKVY2cefXChdFoeeb7-4qEj51dvMKE3YwFLubVw2tVE5V5mKI5Rnvfs7TqBpaU-LIe5K0sfLtOC9KKVJRpxwX8DMGMZNSJDl2xIWvrinbx7aY6gMauFsSAPul0We2oQ65NwJ0giePg-5pNnkUxcWd9oh_RrROWeuBsc72ncFTaPUaNZkijSYoSENe4T6DaoGCXwT9gku17PwkHN8YW9zMFORjBKg9E5ypYWmotWMOTkTOs-0Cg.8VBFpZfhv8JGrCEvoCuEk7HqIESu8TfOJUPnR4w7cag&dib_tag=se&keywords=connector+adapter+for+pin+header&qid=1718053318&s=industrial&sprefix=connector+adapter+for+pin+heade%2Cindustrial%2C111&sr=1-3) for making connections between the Teensy circuit and external wires.
10. 24 V wall adapter [power supply](https://www.amazon.com/gp/product/B095VWHPCC/ref=ppx_yo_dt_b_search_asin_title?ie=UTF8&th=1) for the door solenoid manifold.
11. 12 V wall adapter [power supply](https://www.sparkfun.com/wall-adapter-power-supply-12vdc-600ma-barrel-jack.html) for water valves.
12. [Push buttons](https://www.adafruit.com/product/558) for controlling water valves manually.

<p align="center">

</p>

## Mouse Cameras and Inertial Measurement Unit (IMU)

1. [Video capture devices](https://www.amazon.com/StarTech-com-USB3HDCAP-Video-Capture-Device/dp/B00PC5HUA6/ref=sr_1_3?crid=1AFS4ZNT5DLU3&dib=eyJ2IjoiMSJ9.2LWQRFf16ZPMxyykpqUm1QtyUSt6AnmngN9oj-gAVxMcaWOHj-sg9mHyR_VOyZlGUHDAgP-RiLVpqHIJ-4CsqHQrcvttvKUw0d4jl_iBUglC5TElRCm2L9J60tKoq5Ut_k4KGTKNtWHq8QpZT8mpwddy7JufOzukyDw1aMnpO24DBLibw6otOFhMhWo_Zq9ubgKt0tLhXP5yMT88ZsZAhWJNJHszQvsijkaGipRK1V4.3MNmDwkGFHCEMfpO7wPUEYZ5Zc35iEvtZ5vzg5dQjI0&dib_tag=se&keywords=startech+usb+3.0+hd+video+capture+device+1080p&qid=1743533019&sprefix=startech+usb+3.0+hd+video+capture+device+1080p%2Caps%2C130&sr=8-3) for converting analog video from both the eye and the world cameras into digital video.
2. An analog 5 mm x 5 mm x 3.6 mm [camera](https://www.aliexpress.us/item/3256803738909660.html?spm=a2g0o.detail.pcDetailTopMoreOtherSeller.10.47a4Gmv2Gmv2Vk&gps-id=pcDetailTopMoreOtherSeller&scm=1007.40196.422467.0&scm_id=1007.40196.422467.0&scm-url=1007.40196.422467.0&pvid=40156854-8944-49dc-8f22-28e36af707d0&_t=gps-id:pcDetailTopMoreOtherSeller,scm-url:1007.40196.422467.0,pvid:40156854-8944-49dc-8f22-28e36af707d0,tpp_buckets:668%232846%238108%231977&pdp_ext_f=%7B%22order%22%3A%2273%22%2C%22eval%22%3A%221%22%2C%22sceneId%22%3A%2230050%22%7D&pdp_npi=4%40dis%21USD%2117.62%2110.12%21%21%2117.62%2110.12%21%402101c5b217435439061578444e0ef5%2112000027485322782%21rec%21US%21%21ABXZ&utparam-url=scene%3ApcDetailTopMoreOtherSeller%7Cquery_from%3A) for recoridng the eye of the mouse.
3. An analog 11 mm x 14.1 mm x 13.5 mm [camera](https://www.amazon.com/BETAFPV-Camera-Sensor-1200TVL-Global/dp/B0BMVFGHB1/ref=asc_df_B0BMVFGHB1?mcid=da343b1b22f63402b7daf4ad020d87c1&hvocijid=17462633199980442399-B0BMVFGHB1-&hvexpln=73&tag=hyprod-20&linkCode=df0&hvadid=721245378154&hvpos=&hvnetw=g&hvrand=17462633199980442399&hvpone=&hvptwo=&hvqmt=&hvdev=c&hvdvcmdl=&hvlocint=&hvlocphy=9189768&hvtargid=pla-2281435177658&psc=1) for recording the *world* in front of the mouse head.
4. TDK InvenSense [inertial measurement unit](https://invensense.tdk.com/products/motion-tracking/9-axis/icm-20948/) for measuring the position of the head of the mouse.
5. Intan Technologies RHD 6 ft ultra thin SPI [cable](https://intantech.com/RHD_SPI_cables.html?tabSelect=RHDSPIcables) for video and IMU data.
6. A custom-made **crown** to assemble both cameras and the IMU:
   <p align="center">
   
   
   </p>
7. A custom-made breakout board to send video and IMU data from the **crown** to the video capture devices, and to a custom head motion tracking device, respectively:
   <p align="center">
   
   </p>
8. A custom head motion tracking device, that uses an [Arduino Nano](https://www.digikey.com/en/products/detail/arduino/A000005/2638989?gclsrc=aw.ds&&utm_adgroup=&utm_source=google&utm_medium=cpc&utm_campaign=PMax%20Shopping_Product_Low%20ROAS%20Categories&utm_term=&utm_content=&utm_id=go_cmp-20243063506_adg-_ad-__dev-c_ext-_prd-2638989_sig-Cj0KCQjw_JzABhC2ARIsAPe3ynqEVYD-BFVXE8fA5tr5GG1G9iT6tvCJUC13k_Zf8-BZ9pDcu-J1IRoaAi5cEALw_wcB&gad_source=1&gbraid=0AAAAADrbLljSkpDyIa89TUOGUGG77v6sQ&gclid=Cj0KCQjw_JzABhC2ARIsAPe3ynqEVYD-BFVXE8fA5tr5GG1G9iT6tvCJUC13k_Zf8-BZ9pDcu-J1IRoaAi5cEALw_wcB&gclsrc=aw.ds) board to read data from the IMU, and send them to the Open Ephys I/O board.
   <p align="center">
   
   
   </p>

## Electrophysiology

1. Open Ephys [acquisition board](https://open-ephys.org/acquisition-system/oeps-9029).
2. Open Ephys [I/O Board](https://open-ephys.org/acquisition-system/io-board-pcb), with through-hole vertical female [BNC connectors](https://www.peconnectors.com/coaxial-rf-connectors-bnc-f-rca/hws3912/?srsltid=AfmBOoo6W5EEuw7a9Wj3TCphOwvCRphM8mKeDhZolUMiHQv2XTFZ-yY3QIs&gQT=1) and a surface-mount [HDMI connector](https://www.digikey.com/en/products/detail/amphenol-cs-fci/10029449-111RLF/2785386?s=N4IgTCBcDaIGwAYCcBaALHAjGlmUDkAREAXQF8g) for connection between the custom head motion tracking device and the Open Ephys acquisition board.
3. A male DB15 to terminal breakout board [connector](https://www.amazon.com/DB15-Breakout-Connector-Pin-Male/dp/B073RGHNVD) for connections between single pins in the D-Sub connector to the Open Ephys I/O board. This is how we connected the DB15 pins to the I/O board, and their correspondance to the IMU data pins through the custom head motion tracking device:

<div align = "center">

   | I/O board hole | DB15 pin | IMU pin |
   | :---: | :---: | :---: |
   | gnd | 8 | GND |
   | 1 | 4 | ACC_X |
   | 2 | 12 | ACC_Y |
   | 3 | 5 | ACC_Z |
   | 5 | 13 | GYRO_X |
   | 6 | 6 | GYRO_Y |
   | 7 | 14 | GYRO_Z |

</div>

<p align="center">

</p>

4. A male to female DB15 [cable](https://www.amazon.com/Female-Extension-tinned-Shielded-soliConnector/dp/B093P4W22V/ref=sr_1_5?crid=130GIODUV9ZMD&dib=eyJ2IjoiMSJ9.8Dfuw8gbwaj0Ltt9hNVz6aKSq_yqtXQj2jlV4QmFc4y4sT0Htf3cpZzMWrKl_7DuRt3OoqQtyYHA00QE4swo7XOP6aDjIESvzWZJz_AbNq9HKS9-otb72Ef0sy9F2O8FNDBNScFXaFDjZ9bGLp1yK329s55HWbS-tm0ppJejqisqmffPmw2CRpsBq8liHvQWkC3pBj9iQ86vSZMEVUKZuIpHASC8Zus6WETTaYYXqhI.G9BbIbfxLHvFTva8zR1PQ_lCHkEM7KjyQC1bDxgmQvE&dib_tag=se&keywords=db15%2Bcable%2Bmale%2Bto%2Bfemale%2B3%2Bft&qid=1742251738&sprefix=db15%2Bcable%2Bmale%2Bto%2Bfemale%2B3%2Bft%2Caps%2C152&sr=8-5&th=1) to connect the custom head motion tracking device to the Open Ephys I/O board.
5. An [HDMI cable](https://www.amazon.com/8K-HDMI-Cable-Highwings-Braided/dp/B08NX5CZTF/ref=sr_1_3?crid=2SKNV3K7FT856&dib=eyJ2IjoiMSJ9.0s7nNXqA8Cyls4m55p6IICY9LFpXeLHEcHy1I_FPqAV92uDbZ6TIhbl41YOCkCFidSRUzabDXBDrvh4pv0ZoePQDTtZaBJQwBT6txrHYD13xFO7OUg2KzzUmhyB9yriOJ4LIp5eHkThv963hRvpSOWb0zHB9D1R0EtGbtDyiY9zcurTbybNtn6B363BnccMLb0wQFV-ME9-Ql8XH9SsLLeq9nGqnEYX7qHf7zJj3Bog.j3JsmHsvfzkTRXN6iaeko4XzVftNXnVeqkv6F7fscjs&dib_tag=se&keywords=hdmi%2Bcable&qid=1742258716&sprefix=hdmi%2Bcable%2Caps%2C144&sr=8-3&th=1) to connect the Open Ephys I/O board to the Open Ephys acquisition board.
6. Intan Technologies RHD 6 ft ultra thin SPI [cable](https://intantech.com/RHD_SPI_cables.html?tabSelect=RHDSPIcables) for ephys data.

## Full Rig

<p align="center">
 
</p>

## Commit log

2024-09-11 3D objects added
    [banana.obj, cheese.obj]
2024-09-16 fix obj errors, serial port ID, stim error call
    [banana.obj]
2024-10-23 motion selectivity, valve calibration, fixed 3d object discrimination
    [screenHolders.stl]
2024-10-23 updated codes for LEDs and correct screen number
2024-10-23 LED code fixed
2024-10-28 Rename circuit [top].png to circuit[top].png
2024-11-07 updated valve calibration settings
2025-01-10 camera controls, different time outs
2025-01-17 camera video saving bug fixed
2025-03-07 important update: IR sensors for stimulus added
2025-03-10 config update for stimulus IR sensors
2025-03-21 separate valve parameters, track of stimulus times
2025-03-27 updated circuit board, bottom view
2025-03-27 updated circuit board, top view
2025-04-03 new 3d-printed objects
    [45degreeBracket.stl, doorCylinderStop.stl, doorFloorStop L.stl, doorFloorStop R.stl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]
2025-04-04 missing 3d objects
    [cornerEndBraket.stl, cornerSurfaceBracket.stl, waterPort.stl]
2025-04-16 photo of DB15 and IO board
2025-04-22 HMT device photos
2025-04-22 update for crown cameras IDs
2025-05-14 major upgrade: camera and ephys data acquisition in a different computer
2025-06-03 crown cameras IDs updated
2025-07-08 do not rotate worldCam frame
2025-08-14 bug fix: saving time stamps for crown cameras
